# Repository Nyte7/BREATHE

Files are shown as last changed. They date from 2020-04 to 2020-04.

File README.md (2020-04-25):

# BREATHE

This is a re-usable exhalation valve meant to be retrofitted to non-valve equipped N95 masks or surgical masks.
These were printed using a Creality CR-10 V2 printer with a 0.6mm nozzle.  It has been tested with 3M N95, McCordDick N95, and Benethal N95 masks.

To retrofit an existing mask:

1. Simply cut out a circular hole on the side of your mask that is 3.4cm in diameter.  It's better to start smaller and then gradually cut bigger until the BOTTOM shell part fits snugly (step 2).
2. Place the bottom piece (the one with the spokes) on the inside of the mask through the hole.
3. Attach the top cover piece and rotate clockwise to lock it in place.
4. Prior to disposing your mask, you can remove the valve by rotating the top piece counter-clockwise.  It can be rinsed or sanitized with alcohol or soap/water if need be.

For the gasket material (or inner diaphragm), you can use a TPE rubber sheet that is 1/32 inch or thinner.  It should be cut 3.1cm in diameter.  A tiny hole is then poked in the center of the diaphragm.  The diaphragm is then inserted over the peg in the bottem shell part all the way down and pressed against it so that it remains as flat as possible.

The valve gets tighter as it is rotated to accompany most respirator materials (from thick N95 masks to thin surgical masks).  Don't over-tighten as it may snap.

This is provided for personal use only.  Commercial re-sale of this design is not permitted.

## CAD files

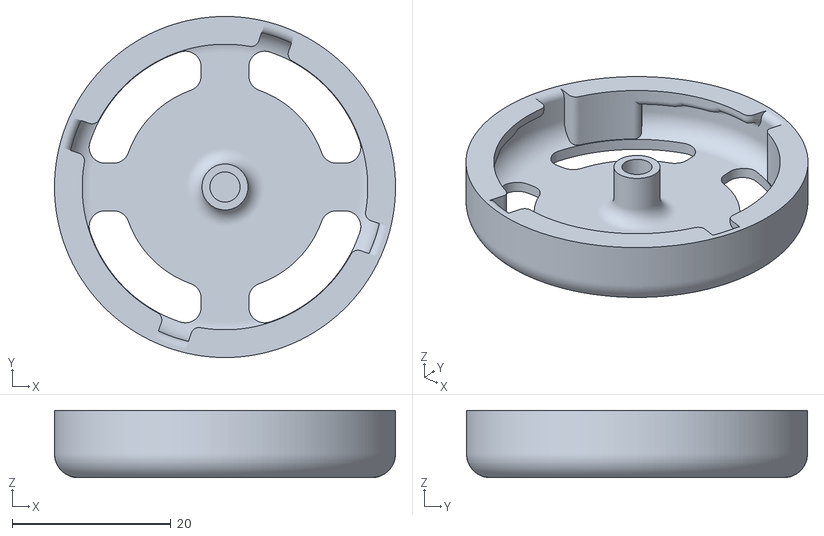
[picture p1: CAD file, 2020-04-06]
TOP V4.stl
43.0 x 43.0 x 8.50

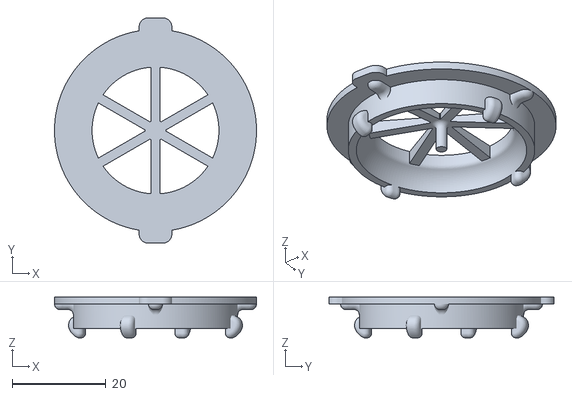
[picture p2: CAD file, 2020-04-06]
BOTTOM V2.stl
43.0 x 48.0 x 8.69

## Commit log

2020-03-26 Initial upload
    [BOTTOM V2.stl, TOP V2.stl]
2020-04-06 Updated STL files
    [BOTTOM V2.stl, TOP V4.stl]
2020-04-06 Removed old STL file
    [TOP V2.stl]
2020-04-06 Update bottom piece slightly
    [TOP V4.stl]
